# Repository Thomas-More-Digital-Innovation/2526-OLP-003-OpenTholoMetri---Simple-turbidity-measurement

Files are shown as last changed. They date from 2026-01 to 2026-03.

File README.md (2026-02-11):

## System Overview

The OpenTholoMetri is a data logging system designed for turbidity measurement using optical sensors. The system operates in a low-power mode, periodically waking up to take sensor readings, logging the data to an SD card with timestamps, and then returning to sleep.

## For more information, visit the [documentation page](https://otm.davidmaat.be) at otm.davidmaat.be.

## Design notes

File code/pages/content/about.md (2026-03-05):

# OpenTholoMetri

OpenTholoMetri is heavily inspired by the [OpenOBS-328](https://github.com/tedlanghorst/OpenOBS-328/tree/main) project by Ted Langhorst. Many thanks to [Olpas](https://www.olpas.tech/) for their support in making this project a reality and to Thomas More Digital Innovation for introducing me to this opportunity.

## System Overview

The OpenTholoMetri is a data logging system designed for turbidity measurement using optical sensors. The system operates in a low-power mode, periodically waking up to take sensor readings, logging the data to an SD card with timestamps, and then returning to sleep.

## Why does this project exist?

While the OpenOBS-328 is great, I found the documentation quite difficult to read. The fact of having to order PCBs (with minimum order quantities) made it hard to justify as a one-off sensor, which makes the accessibility of the sensor lower. That's why: to make water quality measurements accessible to anyone, even if they only want to build a couple. If you need to build these in bulk, I'd strongly recommend looking at the OpenOBS-328 instead.

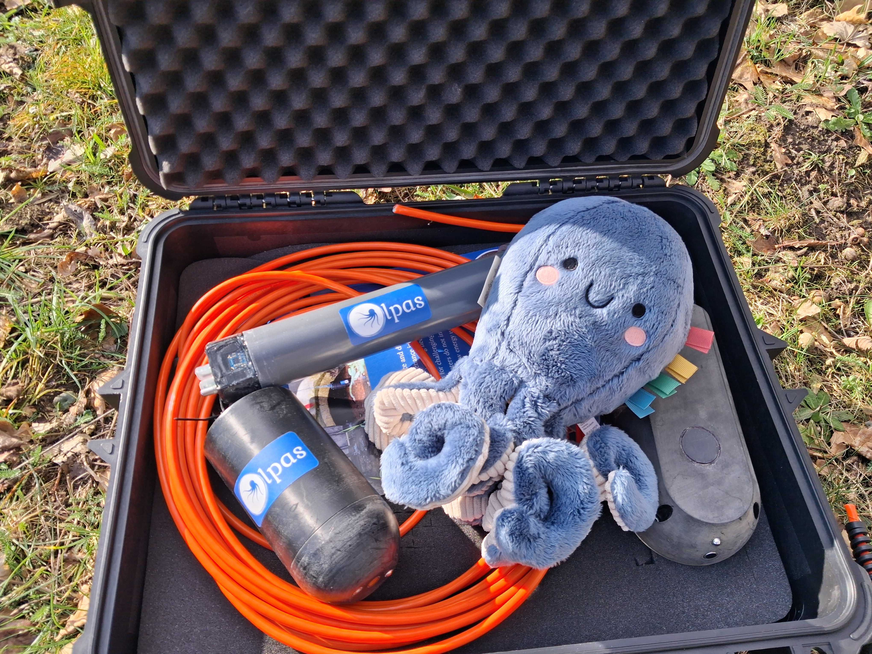
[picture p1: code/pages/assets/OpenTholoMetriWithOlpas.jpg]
OpenTholoMetri with Olpas' other sensors


## Getting started

 - View the materials list [here](/materials-list.html)
 - View the build instructions [here](/build.html)
 - View the code documentation [here](/documentation.html)

## Features

- **Low Power Operation**: Efficient power management for extended battery life
- **Accurate Sensing**: Optical turbidity measurement with proximity and ambient light sensors
- **Data Logging**: Timestamps and sensor readings stored on SD card
- **CSV Export**: Easy-to-analyze data format

## Tools

This project includes tools to help you work with the OpenTholoMetri:

- **<a href="csv-viewer/" target="_blank">CSV Viewer</a>**: A browser-based basic tool to visualize your sensor data

## Data Format

The device generates CSV files with the following format:
- Headers: `Timestamp,Proximity,Ambient Light,Battery Voltage,Temperature (C),Turbidity Raw,Turbidity Voltage`
- Timestamp format: `YYYY-MM-DD HH:MM:SS`
- All measurements are logged at regular intervals

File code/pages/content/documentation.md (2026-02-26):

# Code Documentation

## Overview

The OpenTholoMetri firmware runs on an Adafruit Feather M0 microcontroller and performs:
- Periodic sensor readings at configurable intervals (default: 1 minute)
- Timestamped data logging to SD card in CSV format
- Deep sleep between measurements for power efficiency (~6µA in standby)
- Interrupt-driven wake-up via RTC timer

### Key Features
- **Automated Data Logging**: Periodic sensor readings with configurable intervals
- **Low Power Operation**: Deep sleep mode between readings
- **Real-Time Clock**: Accurate timestamping using PCF8523 RTC
- **Optical Sensing**: VCNL4010 proximity and ambient light sensor
- **Temperature Monitoring**: DS18B20 waterproof temperature probe
- **Power Monitoring**: Battery voltage tracking
- **Interrupt-Driven**: RTC timer-based wake-up mechanism

## Hardware Architecture

### Microcontroller
- **Platform**: SAMD21-based (Adafruit Feather M0)
- **RTC Module**: PCF8523 (on Adalogger FeatherWing, I2C address 0x68)
- **Storage**: SD Card via SPI (on Adalogger FeatherWing)

### Pin Configuration

| Pin | Function | Description |
|-----|----------|-------------|
| 10 | SD_CS_PIN | SD card chip select (SPI) |
| SPI | SCK/MOSI/MISO | SD card data interface (hardware SPI pins) |
| I2C | SDA/SCL | VCNL4010 (0x13) and PCF8523 (0x68) |
| 5 | RTC_INTERRUPT_PIN | RTC countdown timer interrupt (SQW/INT from RTC) |
| 9 | BATTERY_PIN | Battery voltage ADC input (via /2 divider) |
| 12 | DS18B20_POWER_PIN | DS18B20 VCC power control |
| A0 | DS18B20_DATA_PIN | DS18B20 1‑Wire data |
| 13 | GROVE_POWER_PIN | Grove turbidity sensor VCC power control |
| A1 | GROVE_ANALOG_PIN | Grove turbidity sensor analog ADC input |

### Power Consumption

| Mode | Current | Description |
|------|---------|-------------|
| Standby (USB disconnected) | ~6µA | Deep sleep, waiting for RTC interrupt |
| Idle (USB connected) | ~15mA | Light sleep, maintains USB for debugging |
| Active (sensing/logging) | ~12-20mA | Sensor reading and SD write operations |

## Firmware Structure

The code is organized into modular components:

- **`main.ino`** - Main loop handling sleep, RTC interrupts, and sensor reads
- **`RTCManager`** - Manages real-time clock and timer interrupts
- **`SensorManager`** - Reads all sensors (proximity, light, temperature, battery)
- **`SDLogger`** - Writes timestamped data to SD card in CSV format

## Sensor Data

The system reads the following sensors:

- **VCNL4010**: Proximity and ambient light (I2C address 0x13)
  - Proximity: 0-65535 (higher = more turbid)
  - Ambient Light: 0-65535 (lux-equivalent)
- **Grove Turbidity Sensor**: Raw ADC value and calculated voltage
- **DS18B20**: Water temperature in Celsius
- **Battery Monitor**: Supply voltage monitoring

## CSV Output Format

Data is logged with the following columns:

```
Timestamp,Proximity,Ambient Light,Battery Voltage,Temperature (C),Turbidity Raw,Turbidity Voltage
2024-01-15 10:30:00,245,1023,4.15,22.5,512,2.50
```

- **Timestamp**: YYYY-MM-DD HH:MM:SS format
- **Proximity/Ambient Light**: 0-65535
- **Battery Voltage**: Volts
- **Temperature**: Celsius
- **Turbidity Raw**: Raw ADC value
- **Turbidity Voltage**: Calculated sensor voltage

## Configuration

### Changing Logging Interval

Edit `Config.h`:
```cpp
const int SLEEP_INTERVAL = 300;  // Change to desired seconds (300 = 5 minutes)
```

**Considerations**:
- Shorter intervals: More data collection, higher power consumption, larger files
- Longer intervals: Less frequent data, better battery life, smaller files

### Software Installation

#### Required Libraries
Install via Arduino Library Manager:
1. **RTClib** by Adafruit
2. **Adafruit VCNL4010**
3. **SD** (built-in)
4. **SPI** (built-in)
5. **Wire** (built-in)
6. **OneWire**
7. **DallasTemperature**

#### Upload Process
1. Open `main.ino` in Arduino IDE
2. Select board: Adafruit Feather M0
3. Select port: Your COM port
4. Click Upload
5. Open Serial Monitor (115200 baud) to verify initialization

### First-Time Setup

1. **Verify RTC**: Check Serial output shows RTC initialization success
2. **Verify SD Card**: Confirm "SD card initialized successfully!" and `sensor.csv` is created
3. **Test Sensor**: Check for reasonable proximity and light readings
4. **Test Logging**: Wait for first RTC interrupt and verify LED flash and data written to SD card

### Deployment Configuration

For field deployment:
1. Set desired `SLEEP_INTERVAL` in `Config.h`
2. Ensure CR1220 coin cell battery in RTC socket
3. Format fresh SD card (FAT32)
4. Upload final firmware
5. Connect battery and deploy

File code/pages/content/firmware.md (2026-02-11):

## Download or clone the [repository](https://github.com/Thomas-More-Digital-Innovation/2526-OLP-003-OpenTholoMetri---Simple-turbidity-measurement)

## Install Arduino IDE

See [installation instructions](https://support.arduino.cc/hc/en-us/articles/360019833020-Download-and-install-Arduino-IDE)

## Install M0 board library

See [Adafruit installation instructions](https://learn.adafruit.com/adafruit-feather-m0-basic-proto/setup)

## Set measurement values

Set the desired values in [Config.h](https://github.com/Thomas-More-Digital-Innovation/2526-OLP-003-OpenTholoMetri---Simple-turbidity-measurement/blob/main/code/main/Config.h). Don't forget to save!

## Install firmware

Plug in the board via USB, select the board in the Arduino IDE (COMx) and press the Upload button (arrow).

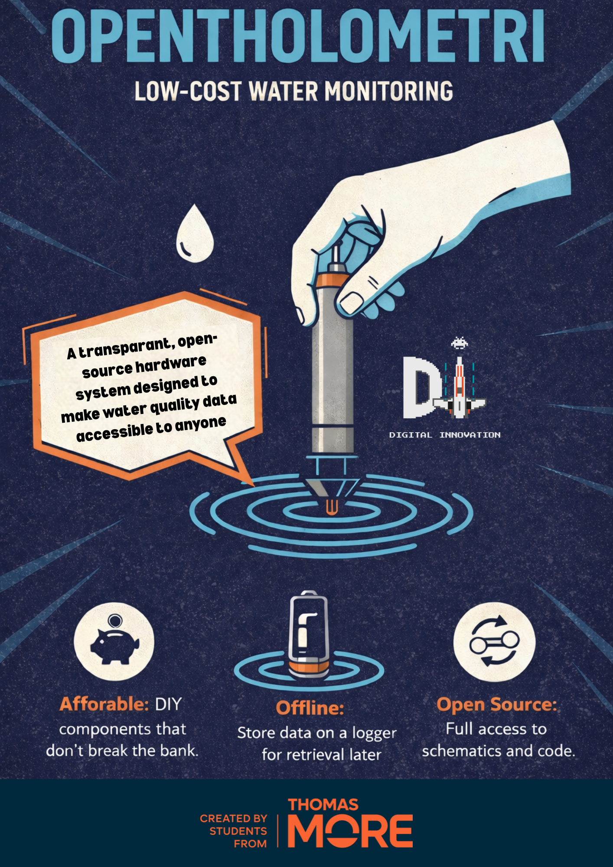
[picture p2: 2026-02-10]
code/pages/assets/poster.png

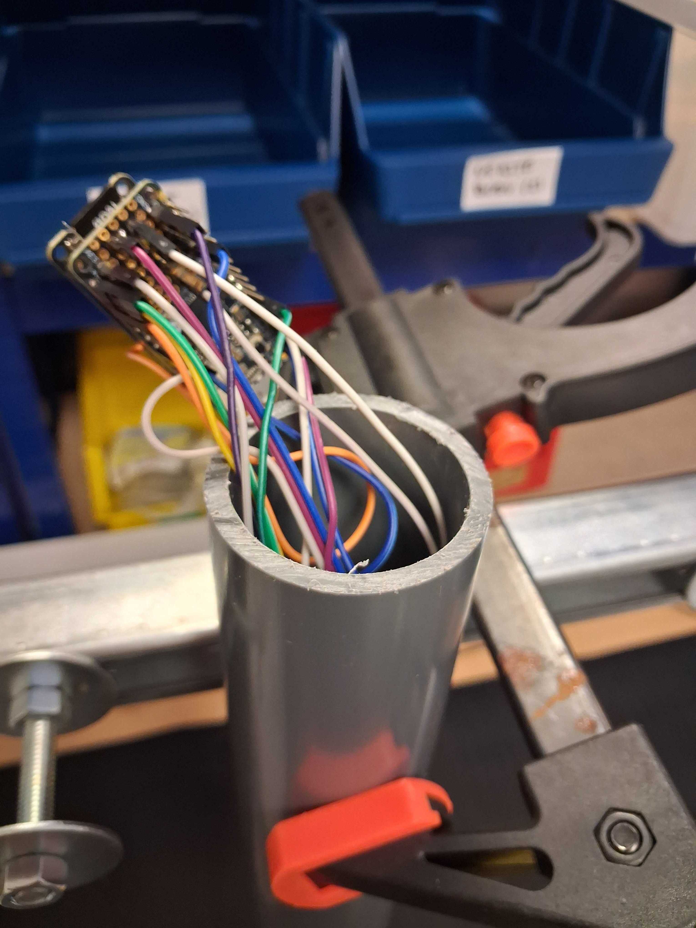
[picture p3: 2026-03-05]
code/pages/assets/epoxy/epoxy-4.jpg

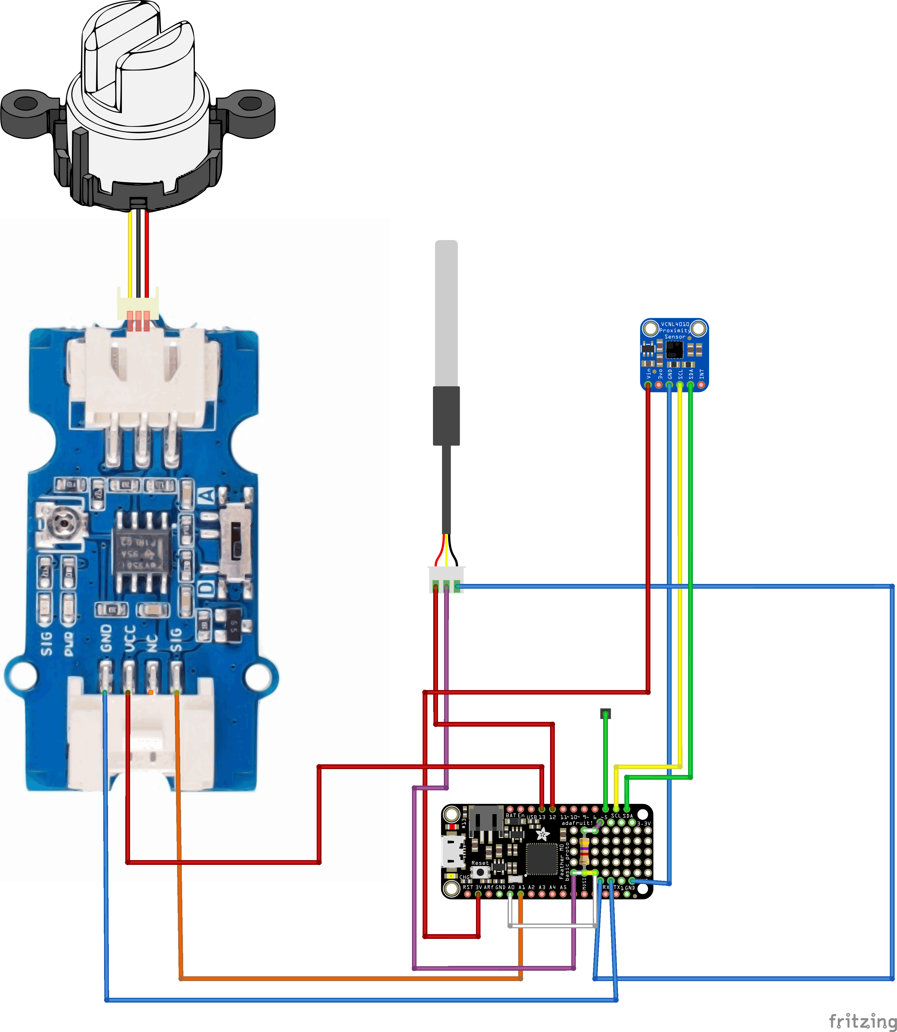
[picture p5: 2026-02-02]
documents/files/Fritzing/OpenTholoMetri electrical layout_bb.png

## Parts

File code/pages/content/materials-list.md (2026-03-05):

# Materials & Tools

### Mechanical Components

- **Sensor Housing**: 3D printed enclosure (files available in repository)
  - Material: PETG
  - Clear UV resistant Epoxy: for waterproofing the sensor
  
### Tools Required

- Soldering iron and (lead-free!!!) solder
- Wire strippers
- 3D printer (or access to 3D printing)

## Bill of Materials (BOM)

| Component | Quantity | Estimated Cost (as of 02-2026) |
| --- | --- | --- |
| [Adafruit Feather M0 Basic Proto - ATSAMD21 Cortex M0](https://www.adafruit.com/product/2772) | 1 | $19.95 |
| [Adalogger FeatherWing - RTC + SD Add-on For All Feather Boards](https://www.adafruit.com/product/2922) | 1 | $8.95 |
| [Header Kit for Feather - 12-pin and 16-pin Female Header Set](https://www.adafruit.com/product/2886) | 1 | $0.95 |
| [Lithium Ion Polymer Battery - 3.7V 350mAh](https://www.adafruit.com/product/2750) | 1 | $6.95 |
| [CR1220 12mm Diameter - 3V Lithium Coin Cell Battery - CR1220](https://www.adafruit.com/product/380) | 1 | $0.95 |
| [512MB micro SD Memory Card](https://www.adafruit.com/product/5252) | 1 | $4.95 |
| [VCNL4010 Proximity/Light sensor](https://www.adafruit.com/product/466) | 1 | $7.50 |
| [Grove - Turbidity Sensor (Meter) for Arduino V1.0](https://www.seeedstudio.com/Grove-Turbidity-Sensor-p-4399.html) | 1 | $24.10 |
| [Waterproof 1-Wire DS18B20 Digital temperature sensor](https://www.adafruit.com/product/381) | 1 | $9.95 |
| Screwable PVC cap | 1 | €1-5 |
| [PVC pipe 50mm](https://www.gamma.nl/assortiment/martens-rio-buis-grijs-50-mm-1-meter/p/B258777) | 1 | €5.49 |
| **Total** | | **$84.15 + €6.49-10.49** |

## Where to Buy

- **Electronics**: DigiKey, Mouser, SparkFun, Adafruit, AliExpress
- **3D Printing**: Local makerspace, online printing services or DIY
- **Hardware**: Local Do-It-Yourself-store or Amazon

## Next Steps

Once you have all materials, proceed to the [Build Instructions](/build.html).

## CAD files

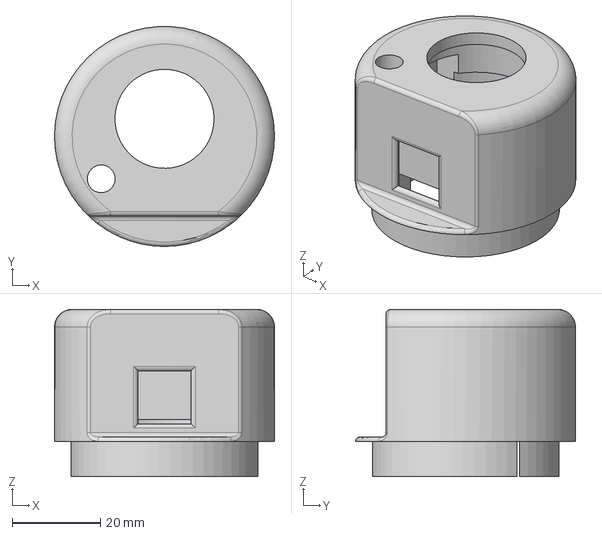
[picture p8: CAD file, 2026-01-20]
documents/files/SensorHead3dFiles/OpenTholoMetriV1.step
50.0 x 50.0 x 38.0 mm

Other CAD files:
documents/files/SensorHead3dFiles/OpenTholoMetriV1.f3d

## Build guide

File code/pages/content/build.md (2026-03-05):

# Build Instructions

## Assembly Overview

Building the OpenTholoMetri takes a couple of hours, spread across a few days. Follow these steps carefully to ensure proper operation.

## 0: Order parts

If you have not already, order the parts listed out in the [BOM](/materials-list.html). If you have everything ready including the tools, follow the guide below :)

## 1: Soldering 

If you don't have much experience soldering, start with the easier parts, like the individual wires. A connection diagram can be found below:

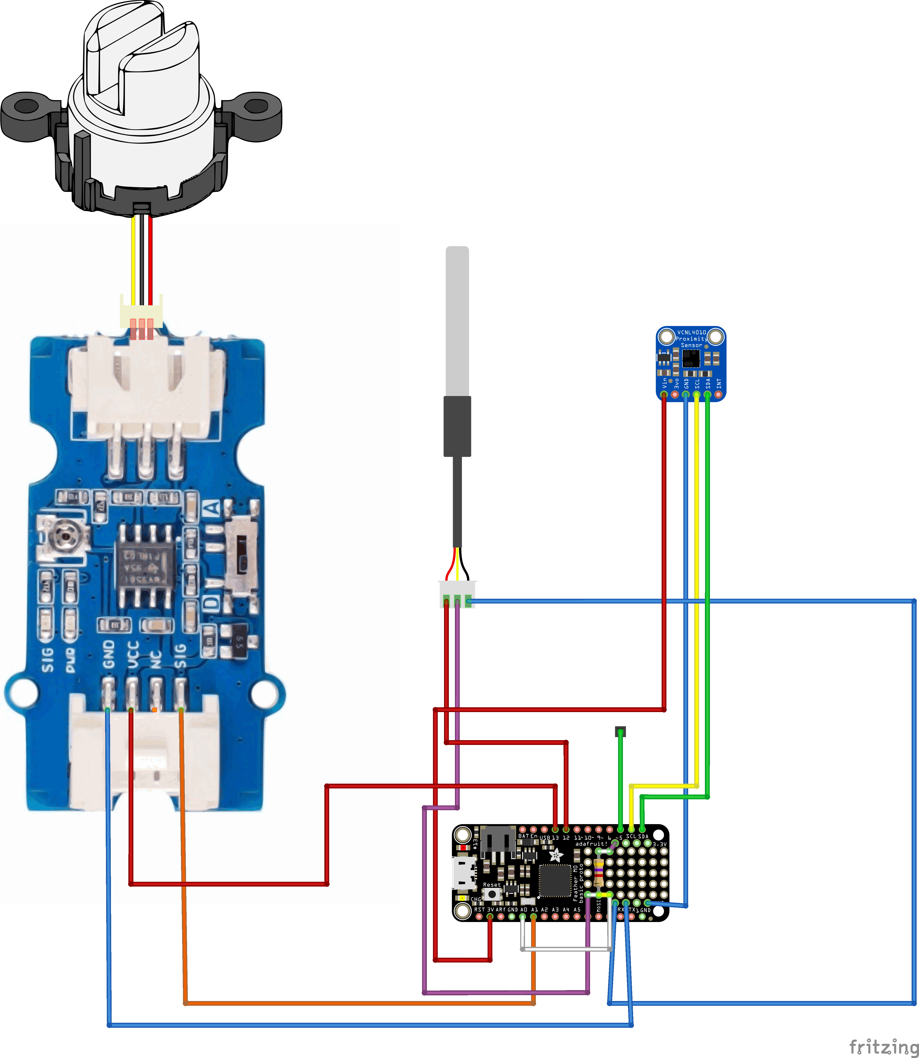
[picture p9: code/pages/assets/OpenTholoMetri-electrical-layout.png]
OTM electrical layout


Solder the individual connections to the Adalogger's second set of pins. The first set is used for the headers to connect the Adalogger to the Feather M0.

## 2: 3D printed housing

3D print the housing from the STEP file provided [here](https://github.com/Thomas-More-Digital-Innovation/2526-OLP-003-OpenTholoMetri---Simple-turbidity-measurement/tree/main/documents/files/SensorHead3dFiles). You can use any 3D printer; be sure to turn on supports if needed for your printer.

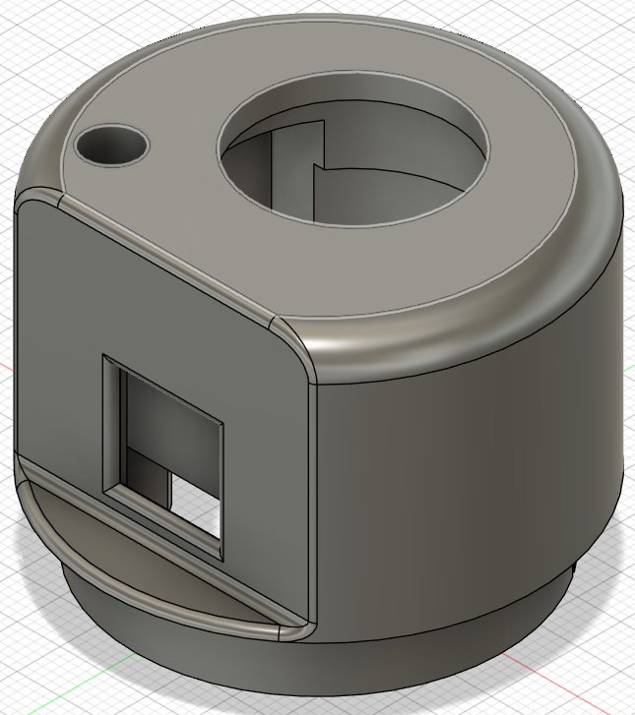
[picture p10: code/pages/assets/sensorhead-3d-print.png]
Sensor head 3d print


## 3: Fitting sensors in housing

Fit the Grove turbidity sensor first, then push in the VCNL4010 and finally fit the DS18B20 probe.

## 4: Pouring the epoxy in the housing

This step takes by far the longest. I did it with two sets of epoxy. The first one is a quick-set epoxy that I used to mount everything; the second is a slow-setting epoxy that is easy to use for this case because it's not very viscous, which means it doesn't need a vacuum pump to be clear.

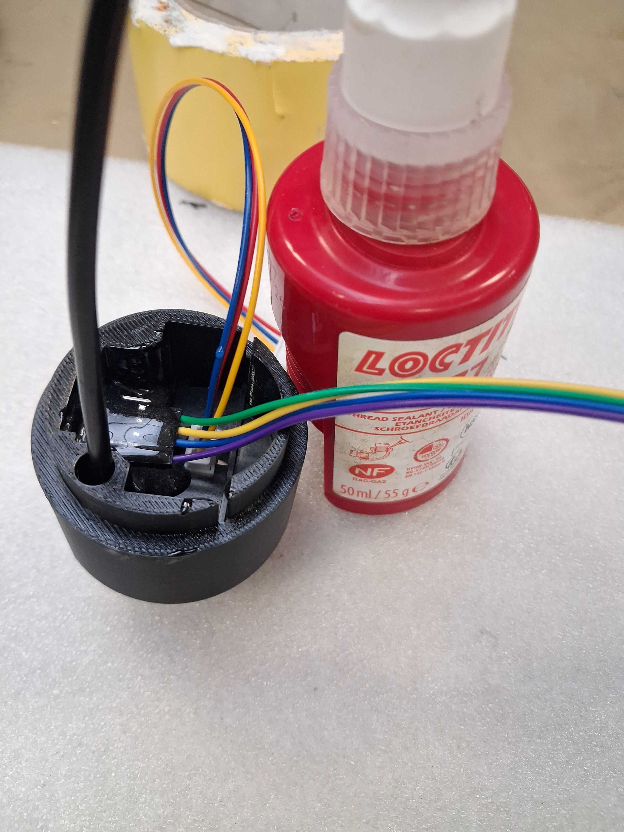
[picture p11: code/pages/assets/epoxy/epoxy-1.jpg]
First epoxy pour


When pouring the final epoxy, make sure the sensor is lying flat. It might need to be poured in two layers due to the epoxy leaking out.

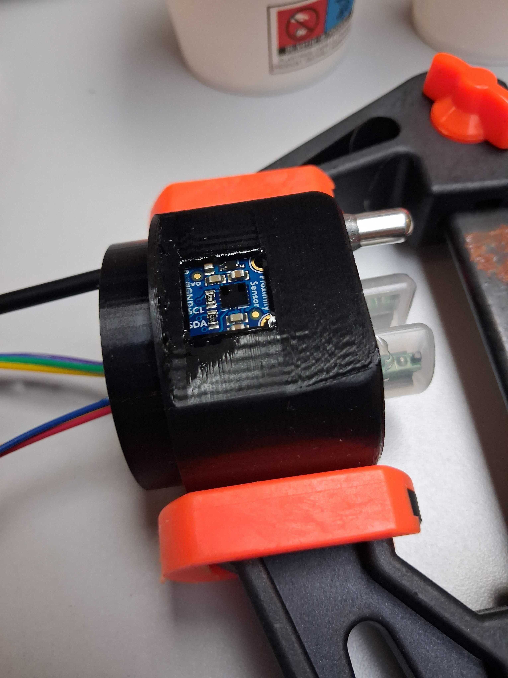
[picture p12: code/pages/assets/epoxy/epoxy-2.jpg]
Second epoxy pour part 1

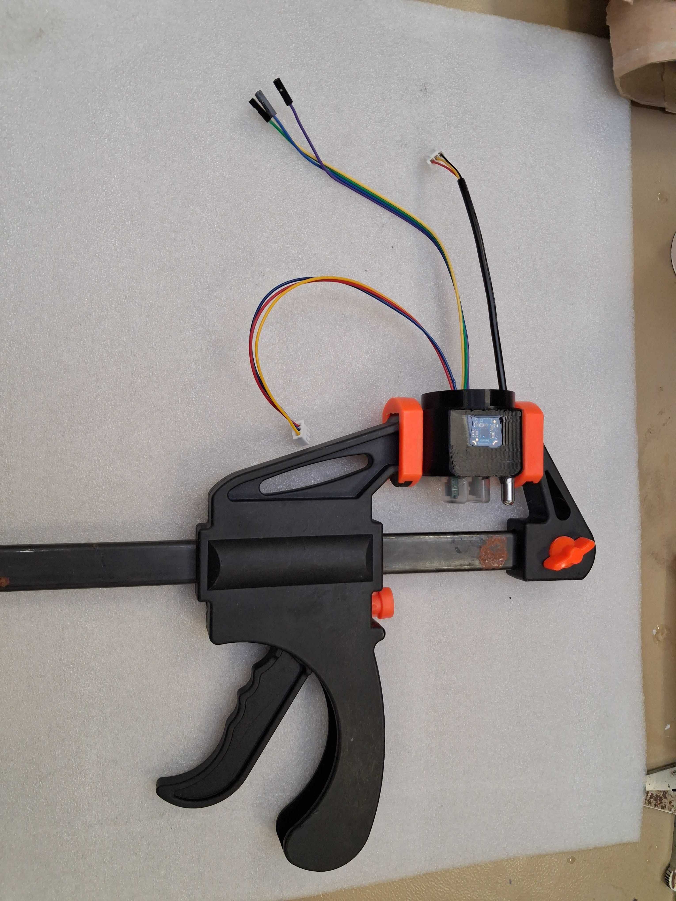
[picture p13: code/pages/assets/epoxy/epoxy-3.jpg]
Second epoxy pour part 2

The picture above is from the first prototype, don't worry about the connections.

## 5: Uploading the firmware to the board

Plug in the board via USB to your computer, then double-click the button on the board (M0). The light will start pulsing and a new USB drive will appear; copy the .uf2 file found [here](https://github.com/Thomas-More-Digital-Innovation/2526-OLP-003-OpenTholoMetri---Simple-turbidity-measurement/tree/main/documents/files/prebuilt-firmware/). This is the firmware with default settings.
If you want to change these, you will have to recompile the firmware; see the [firmware guide](/firmware.html).

## 6: Fitting the head to the tube

Put the boards and wires in the tube, fit the 3d print in the tube, next pour in the expoxy untill the head is sealed.

Head sealing epoxy pour

Make sure to let this epoxy harden fully, because this provides a final seal between the head and tube, protecting the board inside.

## 7: Closing the tube

Finally, fit the cap with pvc glue and close it with teflon to be waterproof.

## 8: Deploy

Charge the boards battery with the USB port and install the sensor at the wanted location.

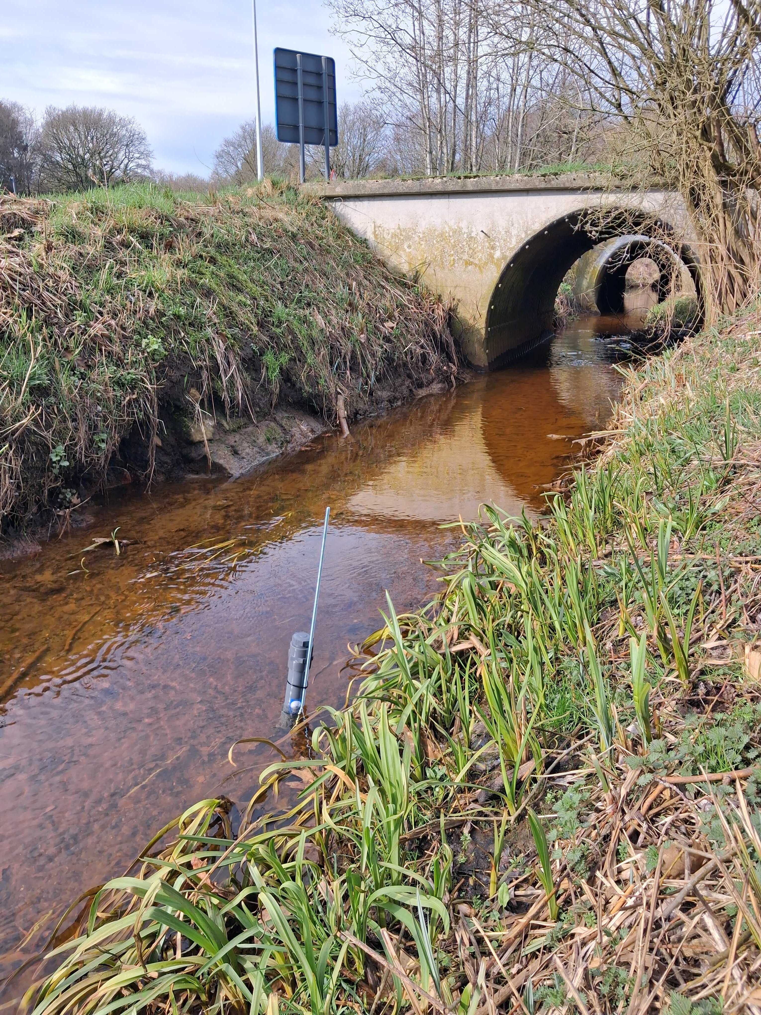
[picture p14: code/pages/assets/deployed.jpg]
Deployed sensor


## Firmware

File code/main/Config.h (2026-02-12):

#ifndef CONFIG_H
#define CONFIG_H

// Pin definitions
const int SD_CS_PIN = 10;        // SD card CS pin on Adalogger
const int LED_PIN = 13;          // LED pin
const int RTC_INTERRUPT_PIN = 5; // RTC interrupt pin (SQW/INT on Adalogger)
const int BATTERY_PIN = 9;       // Battery voltage pin
const int DS18B20_POWER_PIN = 12;   // DS18B20 VCC power control
const int DS18B20_DATA_PIN = A0;    // DS18B20 1-Wire data pin
const int GROVE_POWER_PIN = 13;     // Grove turbidity sensor VCC power control
const int GROVE_ANALOG_PIN = A1;    // Grove turbidity sensor analog pin

// Timing configuration
const int SLEEP_INTERVAL = 60; // seconds between logs

// Measurement configuration
const int MEASUREMENT_COUNT = 5;        // Number of measurements to average
const int MEASUREMENT_INTERVAL_MS = 10; // Milliseconds between measurements

// DS18B20 configuration
const unsigned long DS18B20_POWER_STABILIZATION_MS = 10; // ms to wait after powering sensor

// Grove turbidity sensor configuration
const unsigned long GROVE_POWER_STABILIZATION_MS = 10; // ms to wait after powering sensor

// VCNL4010 configuration (match OpenOBS defaults)
// LED current is in 10mA units: 5 => 50mA
const uint8_t VCNL4010_LED_CURRENT_10MA = 5;
// Proximity measurement rate (matches Adafruit VCNL4010 enum values):
// 0..7 => {1.95, 3.90625, 7.8125, 16.625, 31.25, 62.5, 125, 250} measurements/sec
// OpenOBS default is 250 => 7
const uint8_t VCNL4010_PROX_RATE_VALUE = 7;
// Ambient averaging is log2 of number of conversions: 0=>1, 1=>2, ... 7=>128
const uint8_t VCNL4010_AMBIENT_AVERAGING_LOG2 = 1;
// Continuous ambient conversions (bit 7 in VCNL4010_AMBIENTPARAMETER)
const bool VCNL4010_AMBIENT_CONTINUOUS = true;

// Debug configuration
const bool DEBUG_MODE = true;

// File configuration
static const char *LOG_FILE_NAME = "sensor.csv";

#endif // CONFIG_H

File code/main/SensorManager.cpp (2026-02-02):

#include "SensorManager.h"
#include "Config.h"

#include <Wire.h>

namespace
{
    bool vcnl4010Write8(uint8_t reg, uint8_t value)
    {
        Wire.beginTransmission(VCNL4010_I2CADDR_DEFAULT);
        Wire.write(reg);
        Wire.write(value);
        return Wire.endTransmission() == 0;
    }

    bool vcnl4010Read8(uint8_t reg, uint8_t &value)
    {
        Wire.beginTransmission(VCNL4010_I2CADDR_DEFAULT);
        Wire.write(reg);
        if (Wire.endTransmission(false) != 0)
        {
            return false;
        }

        uint8_t readCount = Wire.requestFrom((int)VCNL4010_I2CADDR_DEFAULT, 1);
        if (readCount != 1 || !Wire.available())
        {
            return false;
        }

        value = Wire.read();
        return true;
    }

    bool vcnl4010SetAmbientAveraging(uint8_t log2Avg)
    {
        if (log2Avg > 7)
        {
            log2Avg = 7;
        }

        uint8_t reg = 0;
        if (!vcnl4010Read8(VCNL4010_AMBIENTPARAMETER, reg))
        {
            return false;
        }

        reg &= 0b11111000;
        reg |= (log2Avg & 0b00000111);
        return vcnl4010Write8(VCNL4010_AMBIENTPARAMETER, reg);
    }

    bool vcnl4010SetAmbientContinuous(bool enable)
    {
        uint8_t reg = 0;
        if (!vcnl4010Read8(VCNL4010_AMBIENTPARAMETER, reg))
        {
            return false;
        }

        reg = (reg & 0b01111111) | ((enable ? 1 : 0) << 7);
        return vcnl4010Write8(VCNL4010_AMBIENTPARAMETER, reg);
    }
}

SensorManager::SensorManager()
    : oneWire(DS18B20_DATA_PIN), ds18b20(&oneWire)
{
}

bool SensorManager::begin()
{
    // Configure ADC for SAMD21 (M0) to 12-bit resolution (0-4095)
    analogReadResolution(12);

    // Initialize DS18B20 power pin
    pinMode(DS18B20_POWER_PIN, OUTPUT);
    digitalWrite(DS18B20_POWER_PIN, LOW);
    pinMode(DS18B20_DATA_PIN, INPUT_PULLUP);

    // Initialize Grove turbidity sensor power pin
    pinMode(GROVE_POWER_PIN, OUTPUT);
    digitalWrite(GROVE_POWER_PIN, LOW);

    // Temporarily power DS18B20 to initialize the Dallas library
    digitalWrite(DS18B20_POWER_PIN, HIGH);
    delay(DS18B20_POWER_STABILIZATION_MS);
    ds18b20.begin();
    digitalWrite(DS18B20_POWER_PIN, LOW);

    Serial.println("DS18B20 sensor initialized successfully!");
    Serial.println("Grove turbidity sensor initialized successfully!");

    // Initialize VCNL4010 sensor
    if (!vcnl.begin())
    {
        Serial.println("VCNL4010 sensor initialization failed!");
        return false;
    }

    // Apply OpenOBS-like defaults (Adafruit begin() sets its own defaults; override them here)
    vcnl.setLEDcurrent(VCNL4010_LED_CURRENT_10MA);
    vcnl.setFrequency((vcnl4010_freq)VCNL4010_PROX_RATE_VALUE);

    bool ambientOk = vcnl4010SetAmbientAveraging(VCNL4010_AMBIENT_AVERAGING_LOG2) &&
                     vcnl4010SetAmbientContinuous(VCNL4010_AMBIENT_CONTINUOUS);

    if (DEBUG_MODE)
    {
        Serial.println("VCNL4010 settings applied: LEDcurrent=" + String(VCNL4010_LED_CURRENT_10MA) + " (x10mA), ProxRate=" + String(VCNL4010_PROX_RATE_VALUE) + ", AmbientAvgLog2=" + String(VCNL4010_AMBIENT_AVERAGING_LOG2) + ", AmbientContinuous=" + String(VCNL4010_AMBIENT_CONTINUOUS ? "true" : "false"));
        if (!ambientOk)
        {
            Serial.println("Warning: failed to apply VCNL4010 ambient settings via I2C register write.");
        }
    }

    Serial.println("VCNL4010 sensor initialized successfully!");
    return true;
}

SensorData SensorManager::readSensors()
{
    SensorData data;
    data.proximity = vcnl.readProximity();
    data.ambientLight = vcnl.readAmbient();

    // Read battery voltage from analog pin
    // Battery voltage goes through a voltage divider (/2), so multiply back
    float measuredvbat = analogRead(BATTERY_PIN);
    measuredvbat *= 2;    // we divided by 2, so multiply back
    measuredvbat *= 3.3;  // Multiply by 3.3V, our reference voltage
    measuredvbat /= 4095; // convert to voltage (12-bit ADC resolution)
    data.batteryVoltage = measuredvbat;

    // Read DS18B20 temperature sensor
    digitalWrite(DS18B20_POWER_PIN, HIGH);
    delay(DS18B20_POWER_STABILIZATION_MS);
    ds18b20.requestTemperatures();
    data.temperatureC = ds18b20.getTempCByIndex(0);
    digitalWrite(DS18B20_POWER_PIN, LOW);

    // Read Grove turbidity sensor
    digitalWrite(GROVE_POWER_PIN, HIGH);
    delay(GROVE_POWER_STABILIZATION_MS);
    data.turbidityRaw = analogRead(GROVE_ANALOG_PIN);
    data.turbidityVoltage = data.turbidityRaw * (3.3 / 4095.0);
    digitalWrite(GROVE_POWER_PIN, LOW);

    return data;
}

SensorData SensorManager::readAveragedSensors(int count, int intervalMs)
{
    uint32_t proximitySum = 0;
    uint32_t ambientLightSum = 0;
    float batteryVoltageSum = 0;
    float temperatureSum = 0;
    uint32_t turbidityRawSum = 0;
    float turbidityVoltageSum = 0;

    // Take multiple measurements
    for (int i = 0; i < count; i++)
    {
        SensorData sample = readSensors();
        proximitySum += sample.proximity;
        ambientLightSum += sample.ambientLight;
        batteryVoltageSum += sample.batteryVoltage;
        temperatureSum += sample.temperatureC;
        turbidityRawSum += sample.turbidityRaw;
        turbidityVoltageSum += sample.turbidityVoltage;

        Serial.println("Measurement " + String(i) + ": Proximity=" + String(sample.proximity) + ", AmbientLight=" + String(sample.ambientLight) + ", BatteryV=" + String(sample.batteryVoltage, 2) + ", TempC=" + String(sample.temperatureC, 2) + ", TurbidityRaw=" + String(sample.turbidityRaw) + ", TurbidityV=" + String(sample.turbidityVoltage, 4));

        // Delay between measurements (skip delay after last measurement)
        if (i < count - 1)
        {
            delay(intervalMs);
        }
    }

    // Calculate averages
    SensorData averaged;
    averaged.proximity = proximitySum / count;
    averaged.ambientLight = ambientLightSum / count;
    averaged.batteryVoltage = batteryVoltageSum / count;
    averaged.temperatureC = temperatureSum / count;
    averaged.turbidityRaw = turbidityRawSum / count;
    averaged.turbidityVoltage = turbidityVoltageSum / count;

    return averaged;
}

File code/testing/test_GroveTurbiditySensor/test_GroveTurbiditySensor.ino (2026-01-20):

// Pin assignments
const int SENSOR_POWER_PIN = 11; // VCC for Grove sensor connected to digital pin 11
const int SENSOR_ANALOG_PIN = A1; // Analog reading on A1
const unsigned long POWER_STABILIZATION_MS = 20; // Time to wait after powering sensor (ms)

void setup() {
  // Initialize serial for debug output
  Serial.begin(9600); // Baud rate: 9600

  // Configure ADC for SAMD21 (M0) to 12-bit resolution (0-4095)
  // and use the 3.3V reference typical for M0 boards.
  analogReadResolution(12);

  // Configure sensor power pin and ensure sensor is off initially
  pinMode(SENSOR_POWER_PIN, OUTPUT);
  digitalWrite(SENSOR_POWER_PIN, LOW);
}

void loop() {
  // Power the sensor
  digitalWrite(SENSOR_POWER_PIN, HIGH);

  // Allow sensor to stabilize after power-up
  delay(POWER_STABILIZATION_MS);

  // Read the analog value from A1 on the M0
  int sensorValue = analogRead(SENSOR_ANALOG_PIN); // raw ADC value (0-4095)

  // Convert the analog reading to voltage using 3.3V and 12-bit resolution
  float voltage = sensorValue * (3.3 / 4095.0);

  // Print raw and voltage values
  Serial.print("Raw: ");
  Serial.print(sensorValue);
  Serial.print("  V: ");
  Serial.println(voltage, 4);

  // Turn sensor power off to save energy
  digitalWrite(SENSOR_POWER_PIN, LOW);

  // Wait until next measurement
  delay(500);
}

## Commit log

2025-12-16 Battery estimation calculation
    [Battery life estimation calculation sheet.xlsx]
2025-12-16 Measuring and logging battery voltage
2026-01-06 Copied sensor values from OpenOBS-328
2026-01-20 3d files for sensor head
    [OpenTholoMetriV1.f3d, OpenTholoMetriV1.step]
2026-02-02 fritzing breadboard layout for documentation
    [OpenTholoMetri electrical layout.fzz]
2026-02-02 ADC 12 bit for battery
2026-02-02 Set power stabilisation to 10ms for grove
2026-02-10 fritzing layout
    [OpenTholoMetri electrical layout.fzz]
2026-02-10 Add materials and build documentation
2026-02-11 material list update
2026-02-12 Change power pin
